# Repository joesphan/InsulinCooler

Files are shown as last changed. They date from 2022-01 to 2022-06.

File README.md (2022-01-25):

# Insulin Cooler

This repository is for my senior project

#### Problem Statement

There is a large population of diabetic citizens who require doses of insulin every day. Long-term portable methods of insulin storage are very expensive.

#### Methodology and Limitations

Insulin must be stored at temperatures from 36&deg;F to 46&deg;F. Using 3d printing to maximalize thermal insulation in the chassis, combined with peltier coolers, lithium-ion batteries and IOT ESP32, it should be reasonably feasible to create a cooler for under $50.

The specs I submitted for my coursework states that the cooler must have a battery life of at least 48 hours. However, I have made it a personal goal to maximize thermal efficiency to achieve two weeks or more.

Using 3d printing, I should be able to create an airgap insulation.

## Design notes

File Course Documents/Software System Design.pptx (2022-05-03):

## Software System Design

EE493
Joesphan Lu

## Summary

Microcontroller Responsibilities
- Insulin temperature regulation
  - Measuring temperature
  - Controlling peltiers
- Datalogging insulin temperature
- Battery management system
  - Battery balancing
- BLE communication
  - Transmission of data and battery status

## Summary (cont’d)

App Responsibilities
- UX – present the user with data
  - Battery status
  - Insulin temperature
    - Realtime and historic

## Tools

- VsCode
  - ESP-IDF SDK for coding, debugging, and flashing
- Gitlab
  - Github desktop for version control frontend
- USB to UART converter
  - FT232RL, CH340G or similar

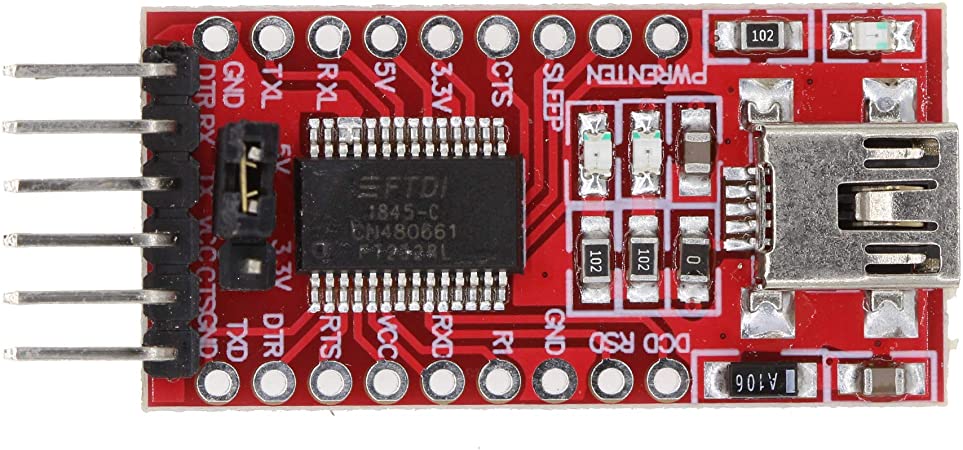
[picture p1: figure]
Amazon.com: FT232RL FTDI USB to TTL 3.3V 5.5V Serial Adapter Module Download Cable for Android Mini Port : Electronics

## MCU Resources

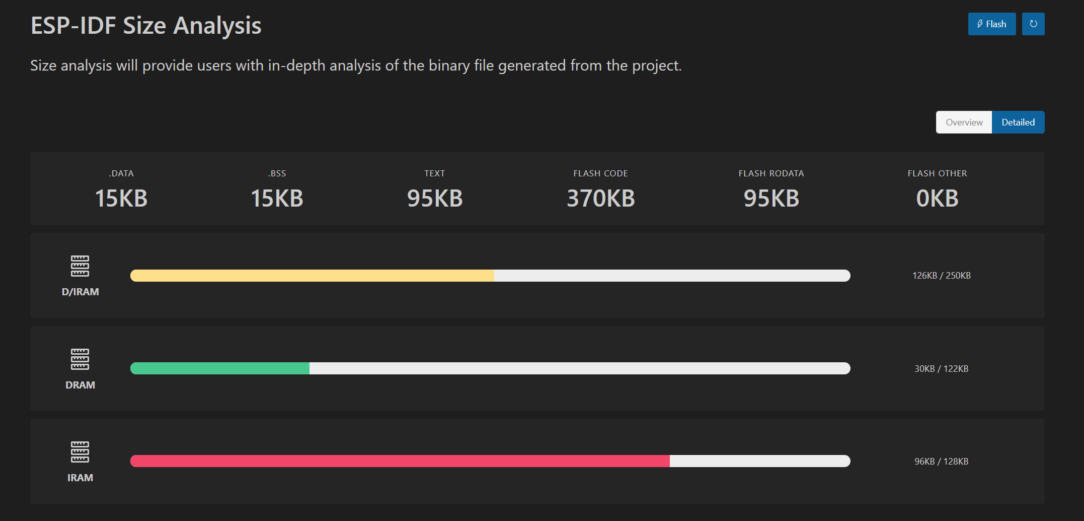
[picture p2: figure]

## Kernel and Task/ISR Design

- freeRTOS
  - BLE SDKs provided by EspressIf use it
  - BLE is the biggest software hurdle
- ISRs:
  - Insulin temperature regulation timer
    - Control peltier coolers on an interval
  - BLE device connection detection
    - Start BLE data transmission
  - USB availability detection
    - Run battery balancing

## Flow-Diagram

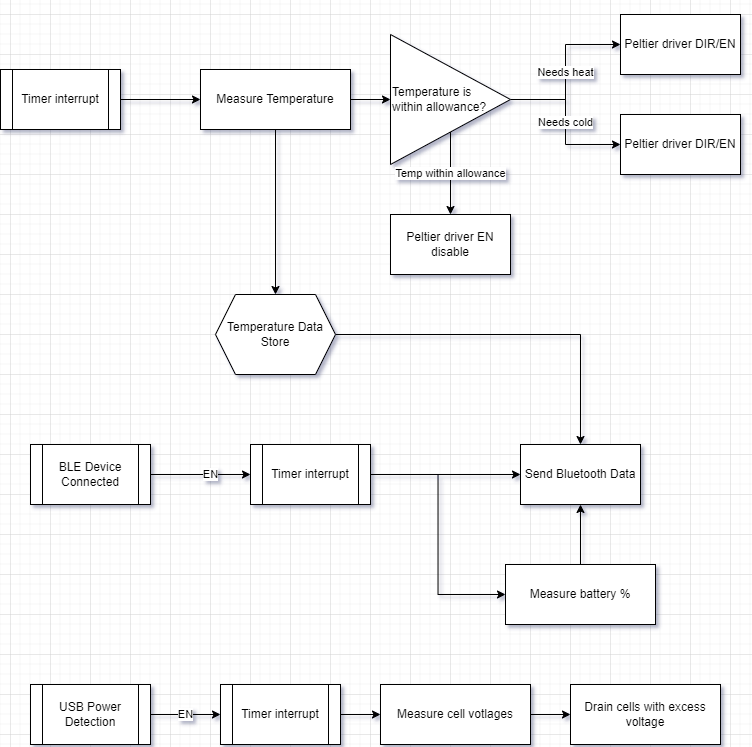
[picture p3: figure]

## Module/Library Description

- TemperatureController
  - Managing temperature of insulin, peltier control
- BatteryMonitor
  - Battery balancing
  - Reads battery percentage
- Datalog
  - Records temperature of insulin to be sent via BLE
- BLESend
  - Send datalogged data to user’s phone

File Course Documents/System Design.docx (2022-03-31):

System Design

Joesphan Lu

BLOCK DIAGRAM

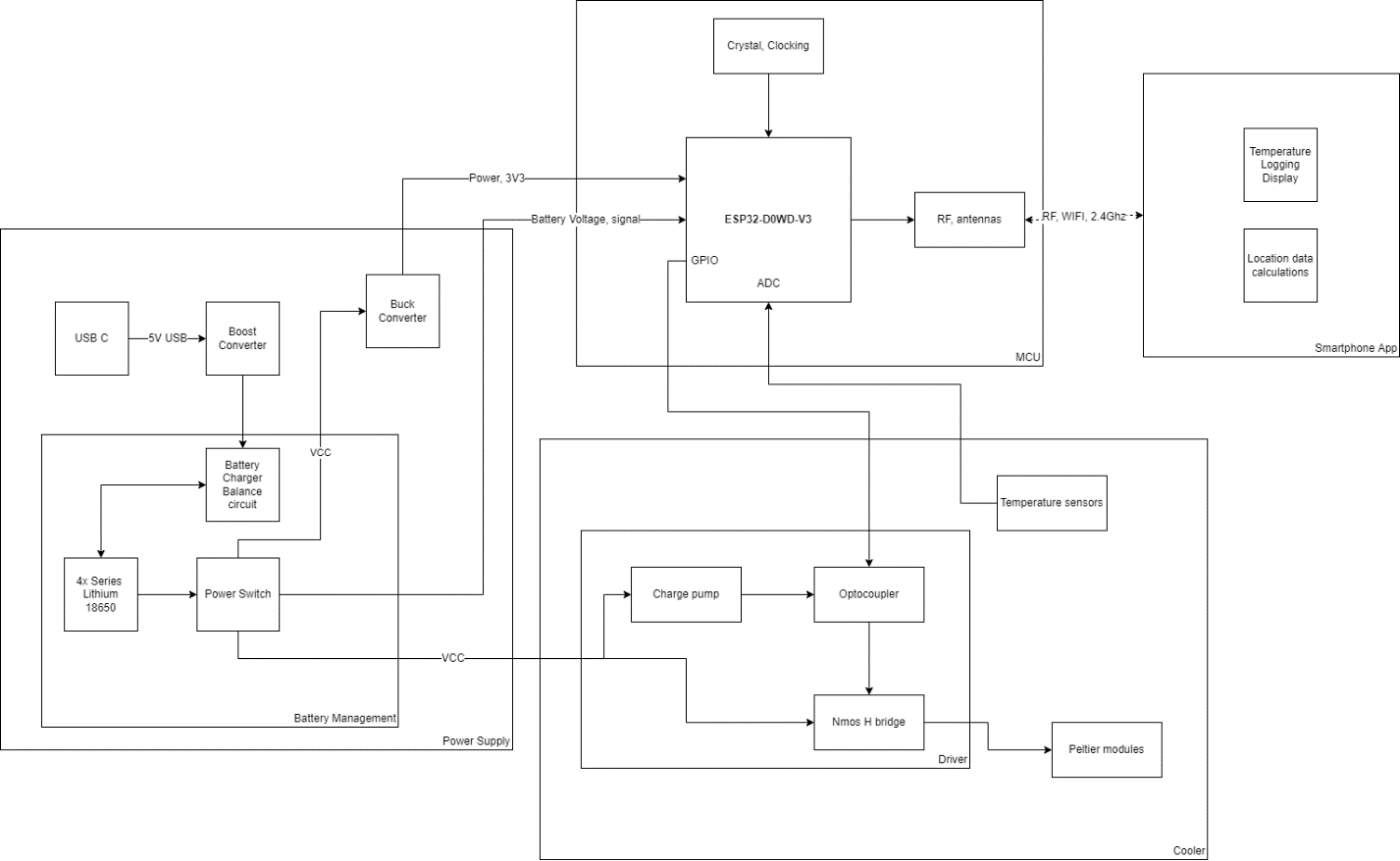
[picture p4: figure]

SUPPLY CURRENTS

Part | Id(3V3) | Id(Unregulated) | Id (USB)
MCU (ESP32-D0WD-V3) ACTIVE RF | 160~260mA | - | -
MCU (ESP32-D0WD-V3) INACTIVE RF | 3~20mA | - | -
Peltier Modules TEC12706 | - | 6A | -
Battery charger | - | - | 3A
Buck converter | - | 0~75mA | -

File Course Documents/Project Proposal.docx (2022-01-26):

Affordable Portable Insulin Cooler

Joesphan Lu

ABSTRACT

The goal of this project is to make an accessible, portable insulin cooler accessible to everybody.

PROBLEM DEFINITION

Insulin coolers on the market today are non-portable and/or very cost prohibitive. Most of them are passive, and not much more than a glorified thermos.

USERS

The users are diabetic people, or anyone who requires insulin to be accessible outside the home, of all financial statuses.

OUTCOMES

Ideally, this project will result in a design that will allow insulin coolers to be accessible to everyone.

FEATURES

-Locating feature, allows user to find the cooler if it’s lost

-Cooling for long periods of time, outperforming passive coolers

-Low cost, affordable to everyone

-Keeps insulin at an appropriate temperature for storage

-Data logging and display available to the user

RISKS

Finding a good compromise between batteries, device longevity, and portability is a major risk, or design challenge. This can be accomplished with more thorough research.

Another risk is the cooling method. Current solutions may not allow efficient cooling. This can be accomplished with running systems at lower duty cycles and/or building a better thermal insulation layer, to achieve higher efficiency.

RESPONSIBILITIES

The device must keep the insulin at an appropriate temperature and must notify the user if the temperature ranges are exceeded. This is critical for the health of the user.

One of the goals of the device is to be low cost. This plays into ethics and making it accessible to everyone.

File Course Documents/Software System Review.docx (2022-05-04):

Software System Review

Joesphan Lu

Summary

The software of the insulin cooler is responsible for controlling the pettier coolers, battery balancing, datalogging, and BLE communications to a phone app.

The phone app is responsible for presenting the user with battery percentage and temperature data.

Tools

Visual Studio code with the ESP-IDF SDK will be used for coding, debugging, and flash programming. Gitlab and Github desktop will be used for revision control.

A generic usb to UART converter will be used as the programmer. CH340G, FT232RL or similar

MCU Resources


On-chip peripherals:

Bluetooth/BLE, PWM, ADC, Radio, RTC/Low Power Management Subsystem

Kernel and Task/ISR design

freeRTOS will be used, as the BLE SDKs by EspressIf use it. The BLE is the biggest software design challenge in this project.

ISRs:

BLE device connection detection, USB power availability, temperature control timer interrupt

Time-Slices TBD

Inter-Task Communications

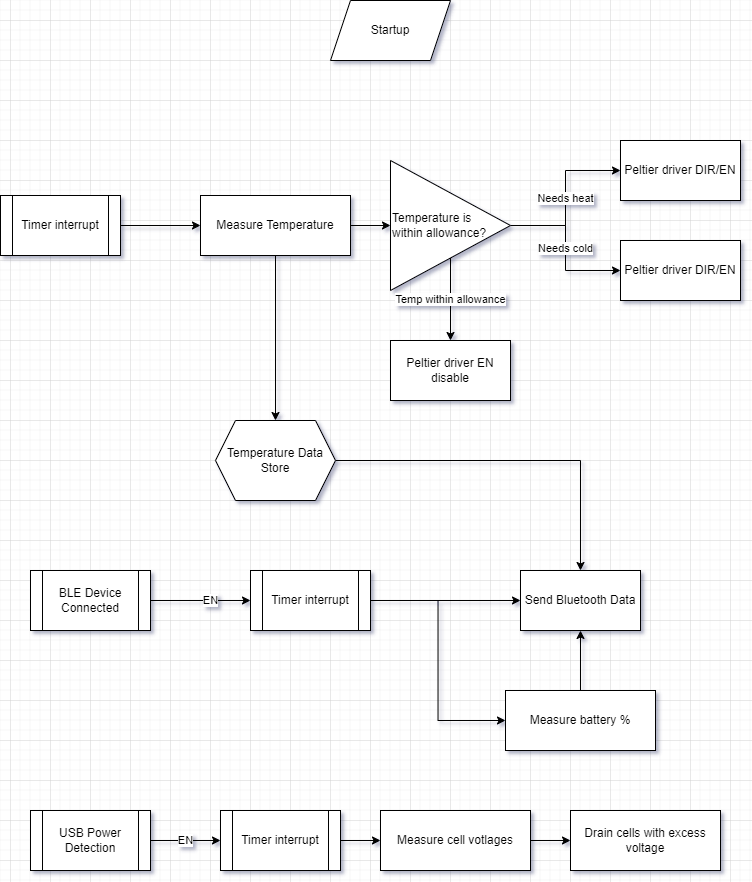
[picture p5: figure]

Module/Library Description

TemperatureControlModule:

Controls temperature of insulin, measures and controls Peltier

BatteryBalancer:

Reads the cell voltage and drains off cells that have excess voltage

BatteryMonitor:

Reads the battery percentage

Datalog:

Records the temperature of insulin, later to be sent via BLE to the mobile device

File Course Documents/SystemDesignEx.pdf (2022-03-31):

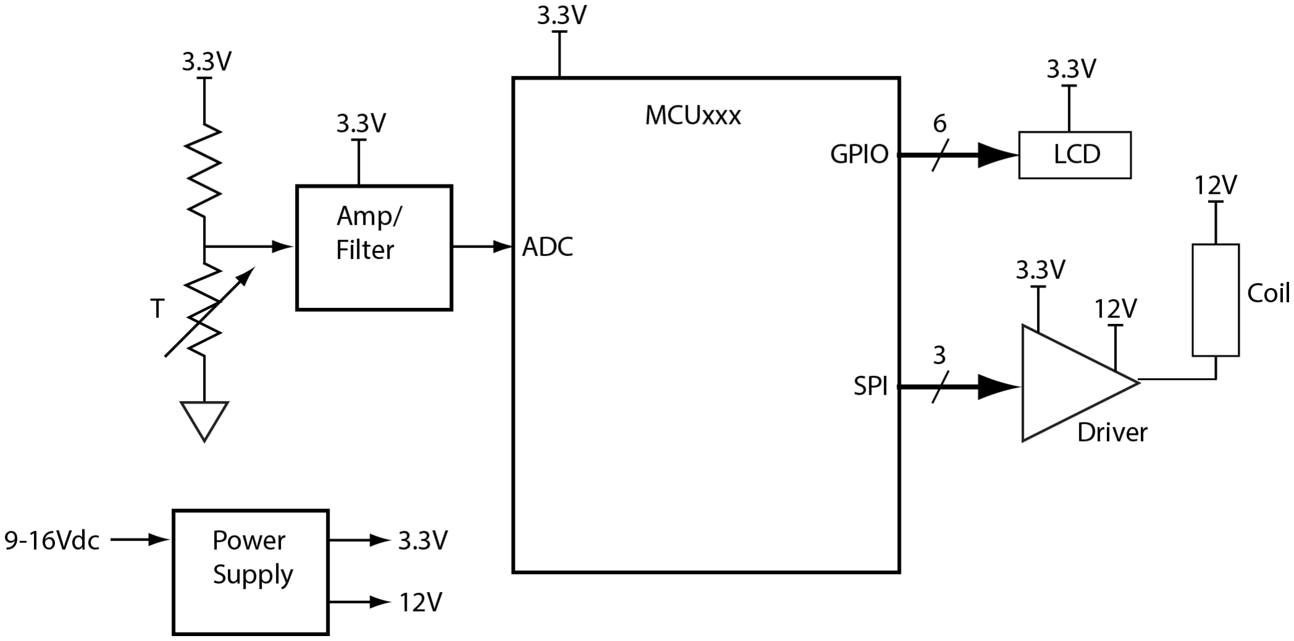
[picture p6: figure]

SystemDesignEx.docx | 1 | 11/23/21

System Design Example

- Based on requirements, the following block diagram was created

Supply Currents

Part | ID (3.3V) | ID (12V) | Dissipation
MCU (K32L2) | 8.7 mA
MCU (K22) | 35.6 mA
LCD | 2.5 mA
OpAmp (LME49721) | 3.25 mA
SallenKey R’s | 4x(3.3/20k)= 660µA
Temp R’s | (10k + 1k) 300µA
MC33879(RUN) | 700 µA | 24 mA | 1.4
MC33879(Sleep) | 700 µA | 5 µA
Coil (20Ω) | | 600 mA
Regulator (Iq)
Total (K32L2) | 16.1 mA | 624 mA

With the numbers shown above, the 3.3V regulator must be able to provide 16.1mA and the 12V regulator (if needed) must provide 624mA.

We still need to determine device power dissipation to see if they’ll get too hot and fail.

SystemDesignEx.docx | 2 | 11/23/21

Power Dissipation
MCU: While the absolute max IO current of +/-25mA, calculations will need to be made to determine if the device will get too hot due to internal R’s in the IOs.

Coil Driver: MC33879, PD, max =1.7W, RDS,on=1.4Ω, Iout,max=1.2A, IxR=1.68W

Coil out, 20ohms, 12/20=600mA, PDIO=600mAx1.4ohms=840mW

150 – 840mWx71 = 90C

Two coils: 30C

Power Supply
- The requirements say that the system must work with a DC input voltage between 9V and 16V

This allows the use of a wide variety of wall adaptors.

- There are two DC output levels required, 3.3V and 12V.
- First, check carefully to see if the coil and driver output supply will work with anything between 9V and 16V. If that is the case, we could go directly to the source without voltage regulation.

Many coil-type devices, solenoids, relays, motors, etc, may work over a wide range of voltages. It may even be worth a reduction in input voltage range if requirements allow.

Regulator 1 – 3.3V, 20mA out, Linear
- Linear – low cost, small size.
- Power out: 3.3 x 20mA = 66mW
- Power in: 16 x 20mA = 320mW
- Power dissipation in regulator: 254mW + Iq
- Efficiency: 66mW/254mW = 26% !

Regulator 1 – 3.3V, 20mA out, Switching
- Power out: 3.3 x 20mA = 66mW
- Efficiency: 85%
- Power in: 77mW, 16 V -> 4.9mA
- Power dissipation in regulator: 11mW + Iq

SystemDesignEx.docx | 3 | 11/23/21

Battery Life
- Requirement: 4 weeks
- Assume coil duty cycle is 0.1, Iavg = 60mA
- Regulator 2, buck-boost, 80% efficient, 75mA in.
- What size battery in mAHr?

With linear regulator 1: Iin = 75mA+20mA = 95mA

Requires: 95mA x 672Hr = 65mAHr

With switching regulator 1: Iin = 75mA+4.9mA = 80mA

Requires: 80mA x 672Hr = 54mAHr

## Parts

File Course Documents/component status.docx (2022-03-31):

Joesphan Lu

Senior Project Component Status

1/20/2022

MFG/SKU | Datasheet packing dwg | Footprint | Symbol

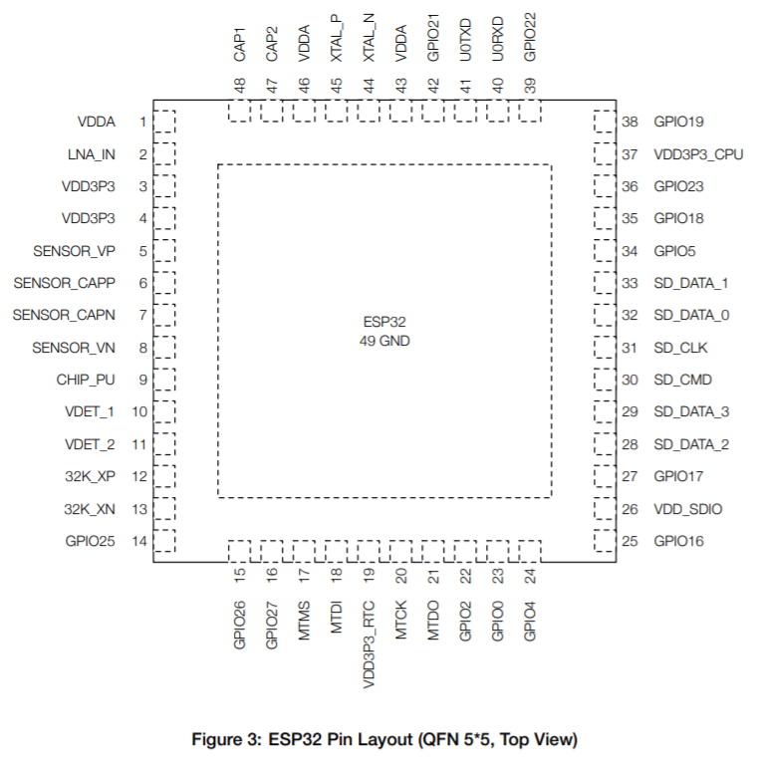
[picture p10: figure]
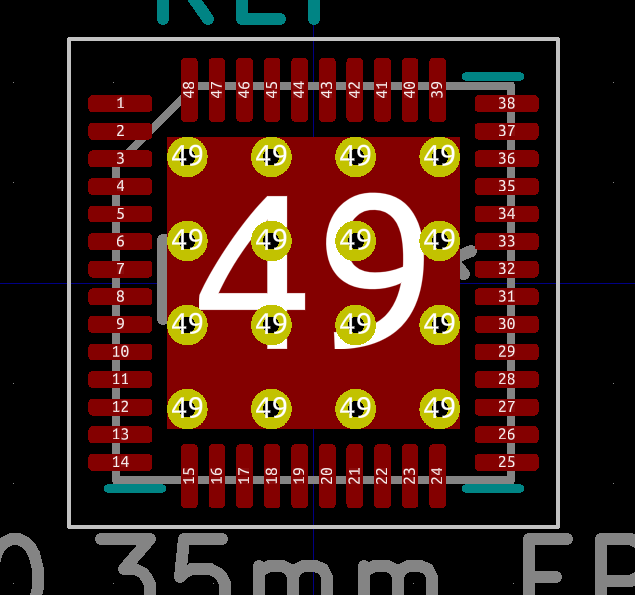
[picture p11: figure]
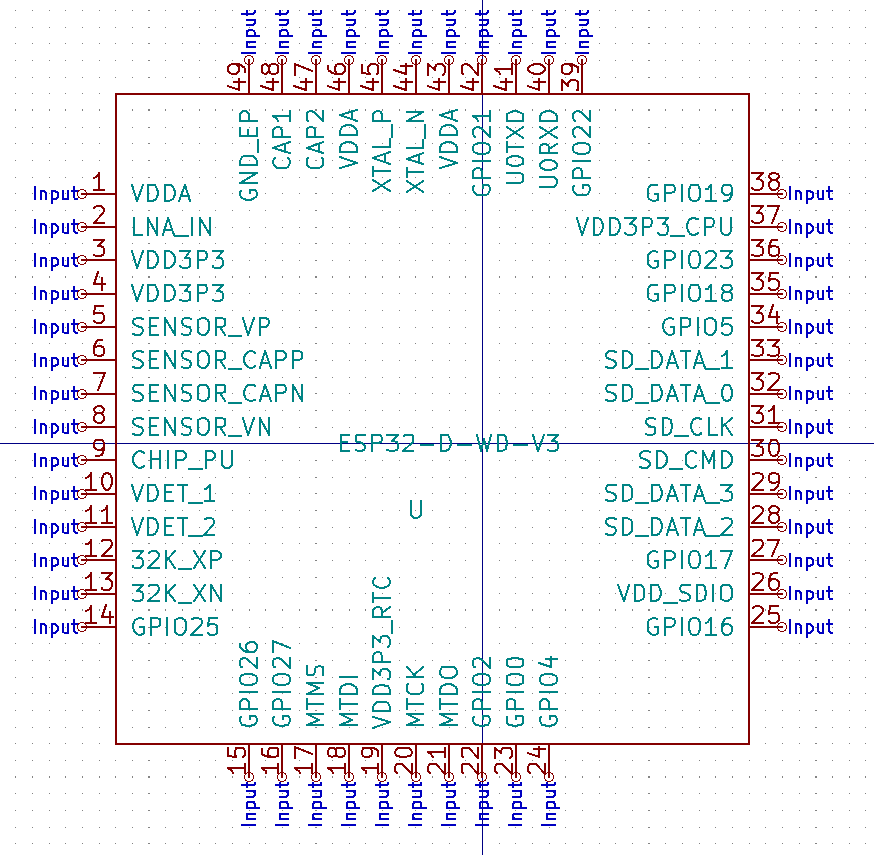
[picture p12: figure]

Espressif ESP32-D0WD-V3

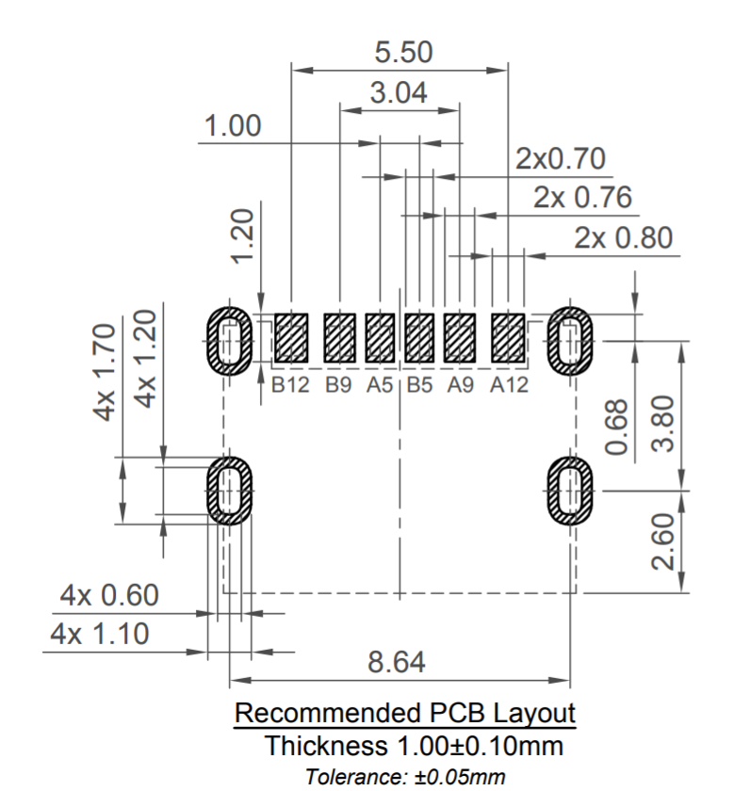
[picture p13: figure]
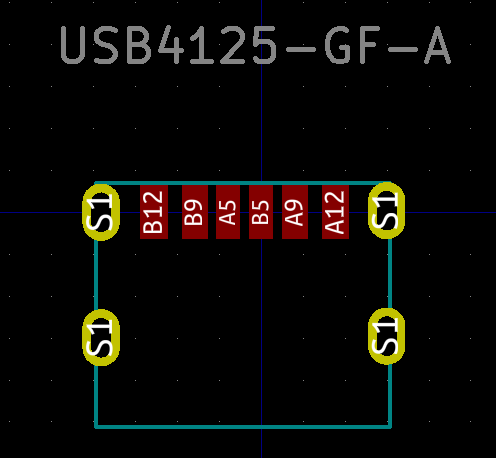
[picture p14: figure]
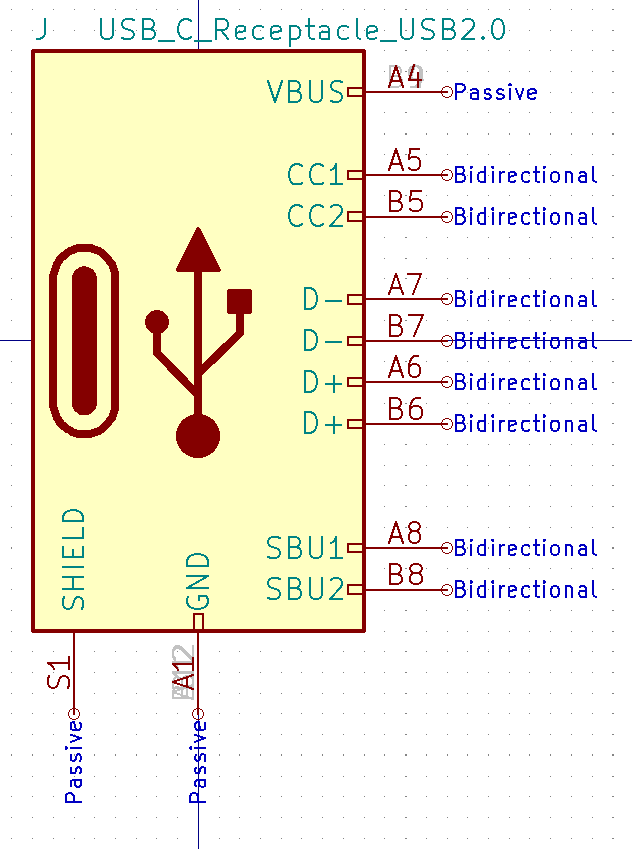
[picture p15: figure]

GCT USB4125-GF-A

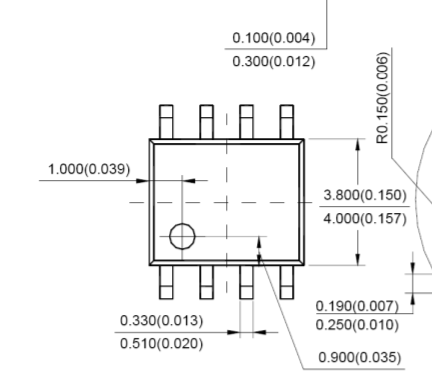
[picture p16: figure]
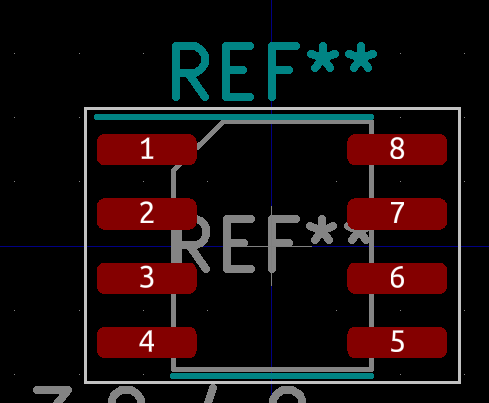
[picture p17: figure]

MaxLinear, Inc. SP34063AEN-L/TR


Raltron Electronics RH100-40.000-10-F-1010-TR


Nexperia USA Inc. BUK9K52-60E | | | Unit A: Unit B:


International Rectifier IRS2103SPBF
Battery charger TBD
Peltier cooler | 2 wires | 1x2 header | 1x2 header

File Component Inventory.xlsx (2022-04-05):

Manufacturer Part Number | Description | Unit Price | Extended Price | Quantity | Ouchies
MIKROE-3828 | PELTIER ELEMENT TEC1-12706 | 5 | $10.00 | 2 | $87.83
ESP32-D0WD-V3 | IC RF TXRX+MCU BLUETOOTH WIFI | 1.8 | $5.40 | 3
USB4125-GF-A | CONN RCPT TYPE C 6P SMD RA | 0.7 | $3.50 | 5
2108838-1 | CHIP ANT., SMD, BT/WI-FI 2.4GHZ | 0.42 | $1.26 | 3
SP34063AEN-L/TR | IC REG BUCK BST ADJ 1.5A 8SOIC | 0.55 | $1.65 | 3
CL32A107MQVNNNE | CAP CER 100UF 6.3V X5R 1210 | 0.68 | $2.04 | 3
SDES064T-221MS | FIXED IND 220UH 640MA 1.04OHM SM | 0.41 | $2.05 | 5
RH100-40.000-10-F-1010-TR | CRYSTAL 40.0000MHZ 10PF SMD | 0.39 | $1.56 | 4
SDNT2012X103F3950FTF | THERM NTC 10KOMH 3950K 0805 | 0.1296 | $3.24 | 25
1N5819-TP | DIODE SCHOTTKY 40V 1A DO41 | 0.264 | $2.64 | 10
73L2R20J | RES 0.2 OHM 5% 1/10W 0603 | 0.086 | $0.86 | 10
BUK9K52-60E,115 | MOSFET 2N-CH 60V 16A LFPAK56D | 0.95 | $3.80 | 4
PAM2305DGFADJ | IC REG BUCK ADJUSTABLE 1A 6DFN | 0.398 | $3.98 | 10
104CDMCCDS-330MC | FIXED IND 33UH 4.1A 92 MOHM SMD | 1.08 | $5.40 | 5
AS431BNTR-G1 | IC VREF SHUNT ADJ 1% SOT23-3 | 0.257 | $2.57 | 10
BSD316SNL6327XT | MOSFET N-CH 30V 1.4A SOT363-6 | 0.105 | $10.50 | 100
MCR100JZHF28R7 | RES SMD 28.7 OHM 1% 1W 2512 | 0.242 | $2.42 | 10
KDV12FR100ET | RES 0.1 OHM 1% 1/2W 1206 | 0.264 | $2.64 | 10
SLG55021-200010V | IC GATE DRVR HIGH-SIDE 8TDFN | 0.4552 | $11.38 | 25
AOZ6662DI | POWER IC EZBUCK | 0.4376 | $10.94 | 25

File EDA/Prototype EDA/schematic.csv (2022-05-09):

Source: | C:\Users\joesp\Documents\GitHub\InsulinCooler\EDA\Prototype EDA\schematic.kicad_sch
Date: | 5/7/2022 4:36:04 AM
Tool: | Eeschema (6.0.2)
Generator: | C:\Program Files\KiCad\6.0\bin\scripting\plugins/bom_csv_grouped_by_value_with_fp.py
Component Count: | 97
Ref | Qnty | Value | Cmp name | Footprint | Description | Vendor
AE1, | 1 | Antenna_Chip | Antenna_Chip | RF_Antenna:Johanson_2450AT18x100 | Ceramic chip antenna with pin for PCB trace
BT1, BT2, BT3, | 3 | Battery_Cell | Battery_Cell | Connector_PinHeader_2.54mm:PinHeader_1x02_P2.54mm_Vertical | Single-cell battery
C1, | 1 | 3.797pF | C | Capacitor_SMD:C_0805_2012Metric_Pad1.18x1.45mm_HandSolder | Unpolarized capacitor
C2, | 1 | 4.64pF | C | Capacitor_SMD:C_0805_2012Metric_Pad1.18x1.45mm_HandSolder | Unpolarized capacitor
C3, | 1 | 3.3nF | C | Capacitor_SMD:C_0805_2012Metric_Pad1.18x1.45mm_HandSolder | Unpolarized capacitor
C4, | 1 | 10nF | C | Capacitor_SMD:C_0805_2012Metric_Pad1.18x1.45mm_HandSolder | Unpolarized capacitor
C5, C8, C10, C11, C16, C17, C21, | 7 | 100nF | C | Capacitor_SMD:C_0805_2012Metric_Pad1.18x1.45mm_HandSolder | Unpolarized capacitor
C6, C7, | 2 | 10pF | C | Capacitor_SMD:C_0805_2012Metric_Pad1.18x1.45mm_HandSolder | Unpolarized capacitor
C9, C12, C15, | 3 | 10uF | C | Capacitor_SMD:C_0805_2012Metric_Pad1.18x1.45mm_HandSolder | Unpolarized capacitor
C13, C14, | 2 | 22uF | C | Capacitor_SMD:C_0805_2012Metric_Pad1.18x1.45mm_HandSolder | Unpolarized capacitor
C18, | 1 | 1uF | C | Capacitor_SMD:C_0805_2012Metric_Pad1.18x1.45mm_HandSolder | Unpolarized capacitor
D4, | 1 | SS34 | D_Schottky | Diode_SMD:D_SMA_Handsoldering | Schottky diode
J1, | 1 | Peltier Connection | Conn_01x02_Female | Connector_PinHeader_2.54mm:PinHeader_1x02_P2.54mm_Vertical | Generic connector, single row, 01x02, script generated (kicad-library-utils/schlib/autogen/connector/)
J2, | 1 | USB_C_Receptacle_USB2.0 | USB_C_PWR_ONLY | 1KicadLib:USB4125-GF-A
J3, J5, J6, J7, J8, | 5 | Conn_01x01_Male | Conn_01x01_Male | 1KicadLib:GatorTestpoint | Generic connector, single row, 01x01, script generated (kicad-library-utils/schlib/autogen/connector/)
J4, J9, J10, J11, | 4 | PROG_PORT | Conn_01x02_Male | Connector_PinHeader_2.54mm:PinHeader_1x02_P2.54mm_Vertical | Generic connector, single row, 01x02, script generated (kicad-library-utils/schlib/autogen/connector/)
L1, | 1 | 1.807nH | L | Inductor_SMD:L_0805_2012Metric_Pad1.15x1.40mm_HandSolder | Inductor
L2, | 1 | 3.3uH NRS5024T3R3NMGJ | L | Inductor_SMD:L_Taiyo-Yuden_NR-50xx_HandSoldering | Inductor
L3, | 1 | 33uH | L | Inductor_SMD:L_10.4x10.4_H4.8 | Inductor
R1, R10, | 2 | 20k | R | Resistor_SMD:R_0805_2012Metric_Pad1.20x1.40mm_HandSolder | Resistor
R2, R3, | 2 | 0 | R | Resistor_SMD:R_0805_2012Metric_Pad1.20x1.40mm_HandSolder | Resistor
R4, | 1 | .1 | R | Resistor_SMD:R_1206_3216Metric_Pad1.30x1.75mm_HandSolder | Resistor
R5, R6, | 2 | 1k | R | Resistor_SMD:R_0805_2012Metric_Pad1.20x1.40mm_HandSolder | Resistor
R7, R34, | 2 | 12.5k | R | Resistor_SMD:R_0805_2012Metric_Pad1.20x1.40mm_HandSolder | Resistor
R8, R9, | 2 | 5.1k | R | Resistor_SMD:R_0805_2012Metric_Pad1.20x1.40mm_HandSolder | Resistor
R12, R15, R16, | 3 | 28.7 | R | Resistor_SMD:R_2512_6332Metric_Pad1.40x3.35mm_HandSolder | Resistor
R17, R18, R19, | 3 | 200 | R | Resistor_SMD:R_0805_2012Metric_Pad1.20x1.40mm_HandSolder | Resistor
R20, R21, R24, | 3 | 90k | R | Resistor_SMD:R_0805_2012Metric_Pad1.20x1.40mm_HandSolder | Resistor
R22, R26, | 2 | 180k | R | Resistor_SMD:R_0805_2012Metric_Pad1.20x1.40mm_HandSolder | Resistor
R23, | 1 | 36k | R | Resistor_SMD:R_0805_2012Metric_Pad1.20x1.40mm_HandSolder | Resistor
R25, | 1 | 4.3k | R | Resistor_SMD:R_0805_2012Metric_Pad1.20x1.40mm_HandSolder | Resistor
R27, | 1 | 68k | R | Resistor_SMD:R_0805_2012Metric_Pad1.20x1.40mm_HandSolder | Resistor
R28, | 1 | 510k | R | Resistor_SMD:R_0805_2012Metric_Pad1.20x1.40mm_HandSolder | Resistor
R29, | 1 | 620k | R | Resistor_SMD:R_0805_2012Metric_Pad1.20x1.40mm_HandSolder | Resistor
R30, | 1 | 200k | R | Resistor_SMD:R_0805_2012Metric_Pad1.20x1.40mm_HandSolder | Resistor
R31, | 1 | 51k | R | Resistor_SMD:R_0805_2012Metric_Pad1.20x1.40mm_HandSolder | Resistor
R33, | 1 | 500 | R | Resistor_SMD:R_0805_2012Metric_Pad1.20x1.40mm_HandSolder | Resistor
R39, | 1 | 150k | R | Resistor_SMD:R_0805_2012Metric_Pad1.20x1.40mm_HandSolder | Resistor
R40, | 1 | 100k | R | Resistor_SMD:R_0805_2012Metric_Pad1.20x1.40mm_HandSolder | Resistor
SW1, | 1 | Power Switch | SW_DIP_x01 | Connector_PinHeader_2.54mm:PinHeader_1x02_P2.54mm_Vertical | 1x DIP Switch, Single Pole Single Throw (SPST) switch, small symbol
TH1, TH2, TH3, | 3 | SDNT2012X103F3950FTF | Thermistor | Resistor_SMD:R_0805_2012Metric_Pad1.20x1.40mm_HandSolder | Temperature dependent resistor
U1, | 1 | ESP32-D-WD-V3 | ESP32-D-WD-V3 | Package_DFN_QFN:QFN-48-1EP_5x5mm_P0.35mm_EP3.7x3.7mm
U2, U7, U8, | 3 | NL17SZ14 | NL17SZ14 | Package_TO_SOT_SMD:SOT-553
U3, U4, | 2 | DMT3020LSDQ | DMT3020LSDQ | Package_SO:SO-8_3.9x4.9mm_P1.27mm
U5, | 1 | LM324 | LM324 | Package_SO:SOIC-14_3.9x8.7mm_P1.27mm | Low-Power, Quad-Operational Amplifiers, DIP-14/SOIC-14/SSOP-14
U6, U18, | 2 | slg55021 | slg55021 | 1KicadLib:TDFN_8_2x2mm_EP_0.9x1.65mm
U9, U10, U11, U20, U21, | 5 | BSD316 | BSD316 | Package_TO_SOT_SMD:SOT-363_SC-70-6_Handsoldering
U12, U13, U14, | 3 | PC817 | PC817 | Package_DIP:DIP-4_W7.62mm | DC Optocoupler, Vce 35V, CTR 50-300%, DIP-4
U15, | 1 | AS431 | AS431 | Package_TO_SOT_SMD:SOT-23-5_HandSoldering
U16, | 1 | AP63203WU | AP63203WU | Package_TO_SOT_SMD:TSOT-23-6 | 2A, 1.1MHz Buck DC/DC Converter, fixed 3.3V output voltage, TSOT-23-6
U17, | 1 | XL6009 | XL6009 | Package_TO_SOT_SMD:TO-263-5_TabPin3
U19, | 1 | HT75xx-1-SOT89 | HT75xx-1-SOT89 | Package_TO_SOT_SMD:SOT-89-3 | 100mA Low Dropout Voltage Regulator, Fixed Output, SOT89
U22, | 1 | W25Q40CL | W25Q40CL | Package_SO:SOIC-8W_5.3x5.3mm_P1.27mm
Y1, | 1 | Crystal_GND24 | Crystal_GND24 | Crystal:Crystal_SMD_SeikoEpson_FA238-4Pin_3.2x2.5mm_HandSoldering | Four pin crystal, GND on pins 2 and 4

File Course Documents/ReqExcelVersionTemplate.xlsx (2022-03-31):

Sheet: Summary
Requirement Number and Version | Approved | Verf Required | Verf Plan | Verf Done | Verf Met | Requirement | Comments
1.a | 0.000 |  |  |  |  | The portable insulin cooler shall be able to charge via USB
1.1.a | 0.000 |  |  |  |  | 0.000
2.a | 0.000 |  |  |  |  | The portable insulin cooler must fit in a pair of Calvin Klein 34x34 jeans
3.a | 0.000 |  |  |  |  | The portable insulin cooler shall hold 5 or more cartridges
4.a | 0.000 |  |  |  |  | The portable insulin cooler shall have a location tracking method
5.a | 0.000 |  |  |  |  | The portable insulin cooler shall have a temperature logging and display
6.a | 0.000 |  |  |  |  | The battery needs to last at least 24 hours

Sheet: 1.a
User Requirement
Project Name: | Portable Insulin Cooler
Originator: | Joesphan Lu
Approved:
User Requirement Text: | The portable insulin cooler shall be able to charge via USB
Rationale: | USB is convienient

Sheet: 1.1.a
Technical Requirement | TEMPLATE
Project Name:
Originator:
Approved:
User Requirement Text:
Rationale and Assumptions:
Verification Required:
Verification Plan and Verification Data:

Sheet: 2.a
User Requirement
Project Name: | Portable Insulin Cooler
Originator: | Joesphan Lu
Approved:
User Requirement Text: | The portable insulin cooler must fit in a pair of Calvin Klein 34x34 jeans
Rationale: | Must be portable enough

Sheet: 3.a
User Requirement
Project Name: | Portable Insulin Cooler
Originator: | Joesphan Lu
Approved:
User Requirement Text: | The portable insulin cooler shall hold 5 or more cartridges
Rationale: | Reasonably sized supply

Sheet: 4.a
User Requirement
Project Name: | Portable Insulin Cooler
Originator: | Joesphan Lu
Approved:
User Requirement Text: | The portable insulin cooler shall have a location tracking method
Rationale: | In case it be lost, one can find relatively quickly

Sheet: 5.a
User Requirement
Project Name: | Portable Insulin Cooler
Originator: | Joesphan Lu
Approved:
User Requirement Text: | The portable insulin cooler shall have a temperature logging and display
Rationale: | The user needs to be able to decide if they the insulin has been appropriately refrigerated

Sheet: 6.a
User Requirement
Project Name: | Portable Insulin Cooler
Originator: | Joesphan Lu
Approved:
User Requirement Text: | The battery needs to last at least 24 hours
Rationale: | Long enough to get through a day

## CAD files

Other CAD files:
Chassis 3d model/OldVersions/main.0001.ipt
Chassis 3d model/main.ipt
Part1.ipt

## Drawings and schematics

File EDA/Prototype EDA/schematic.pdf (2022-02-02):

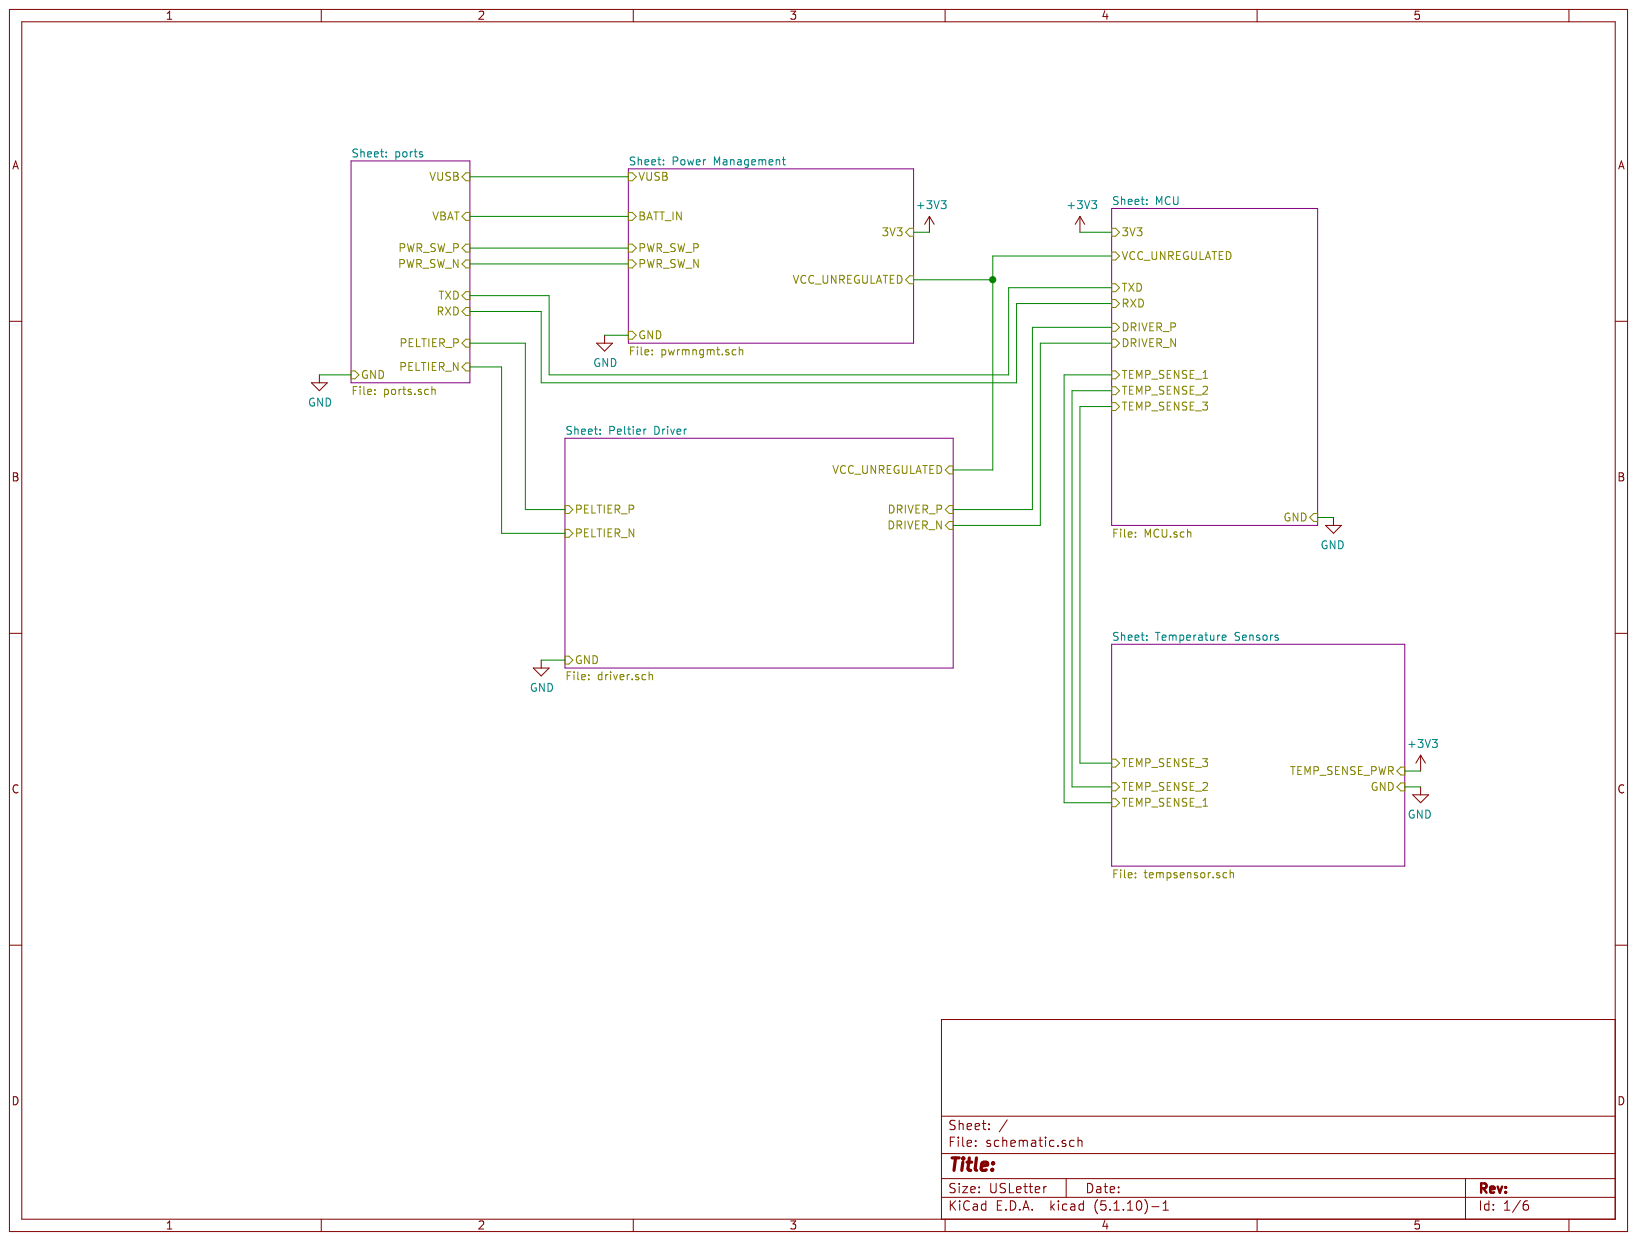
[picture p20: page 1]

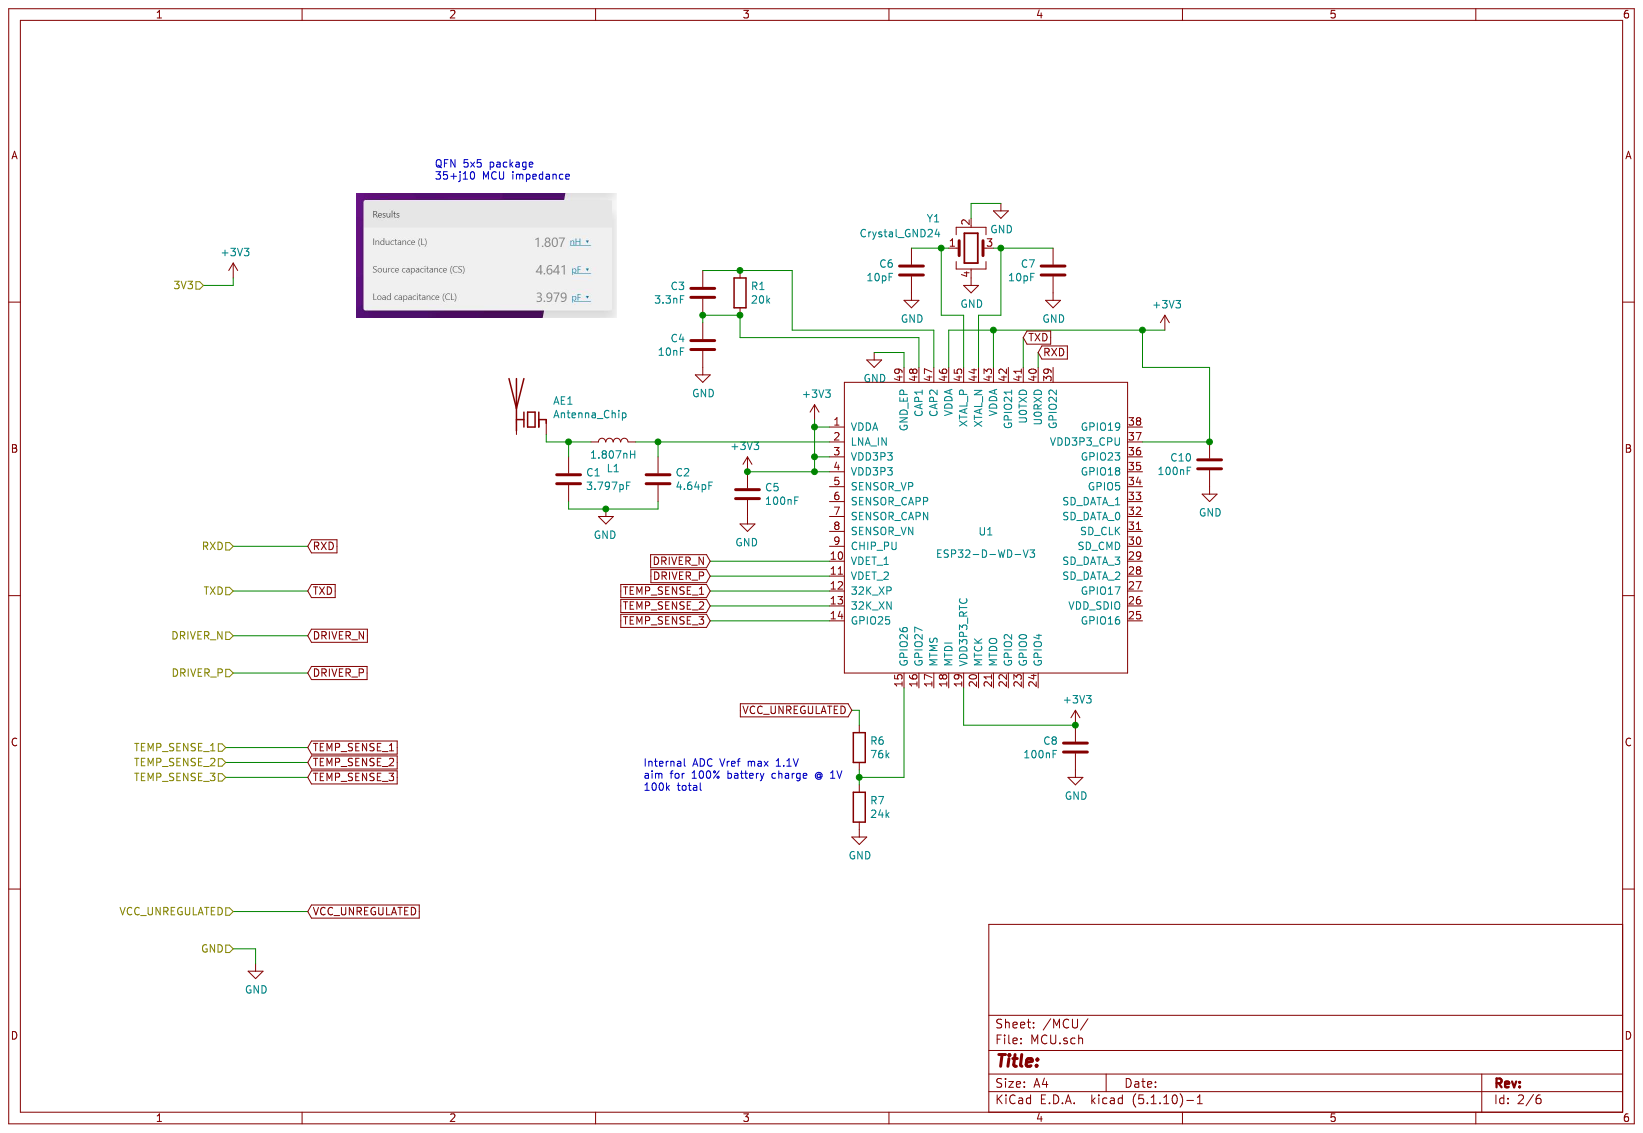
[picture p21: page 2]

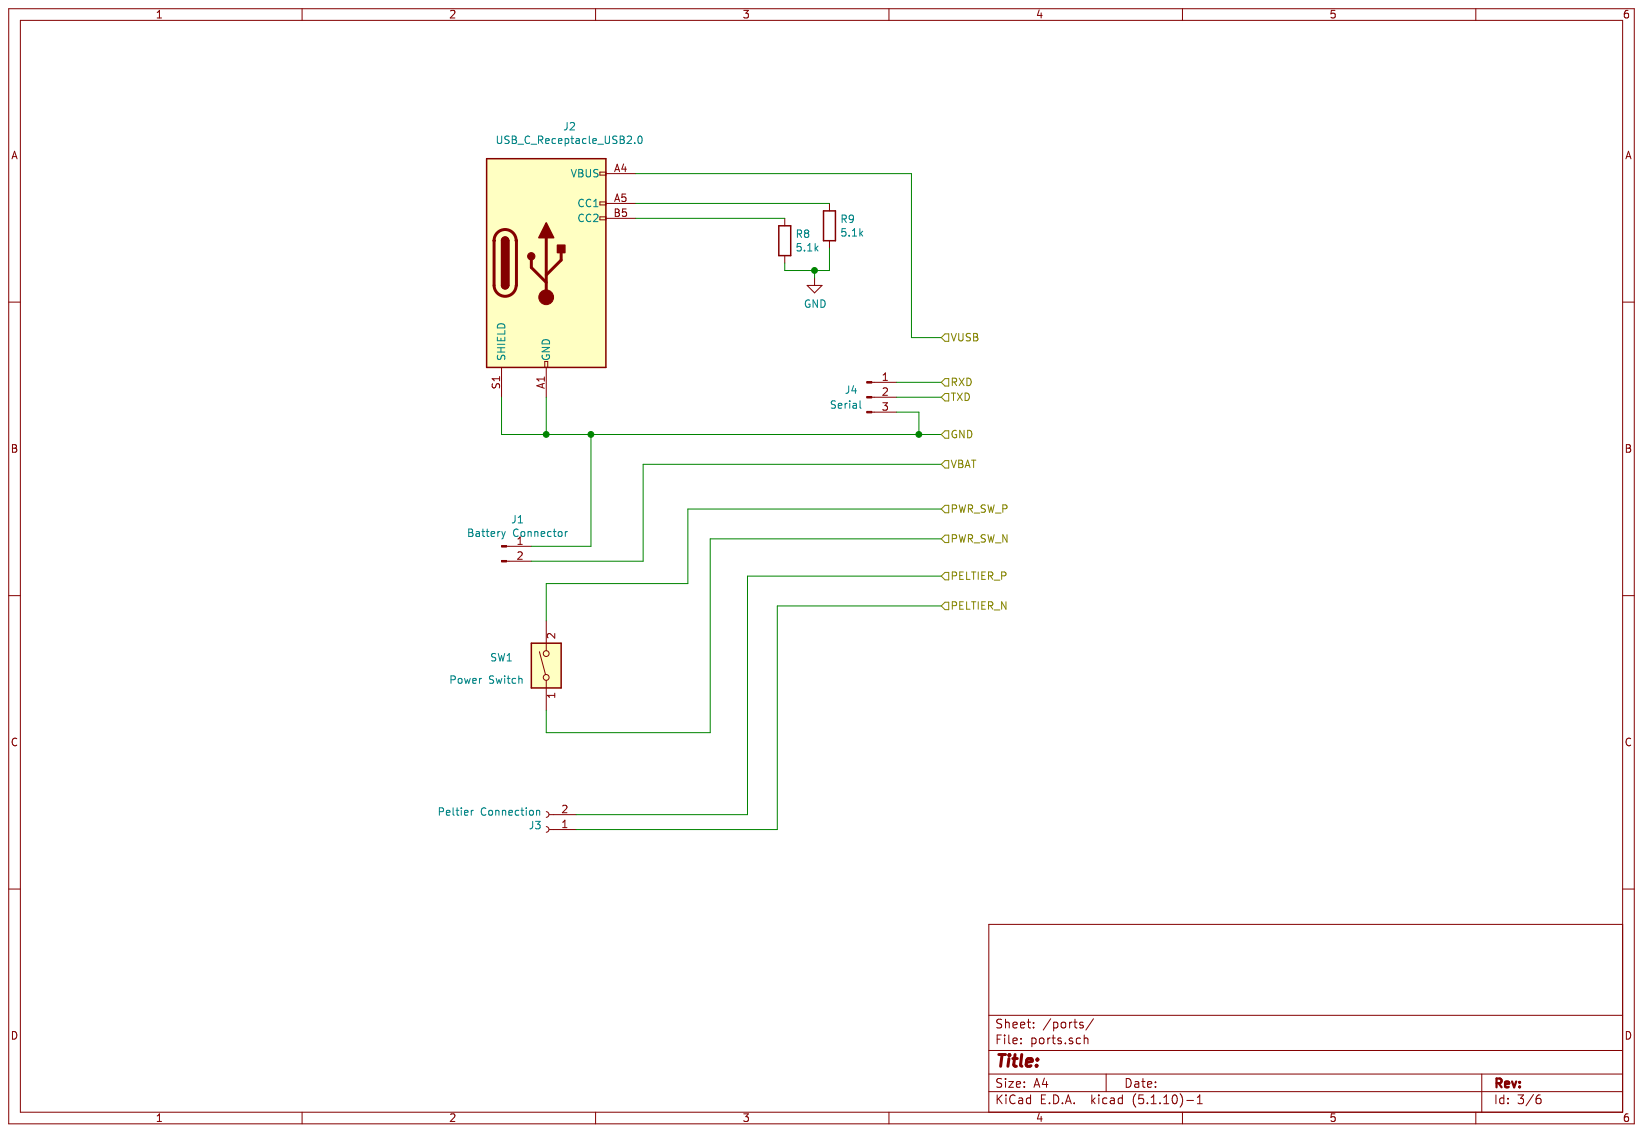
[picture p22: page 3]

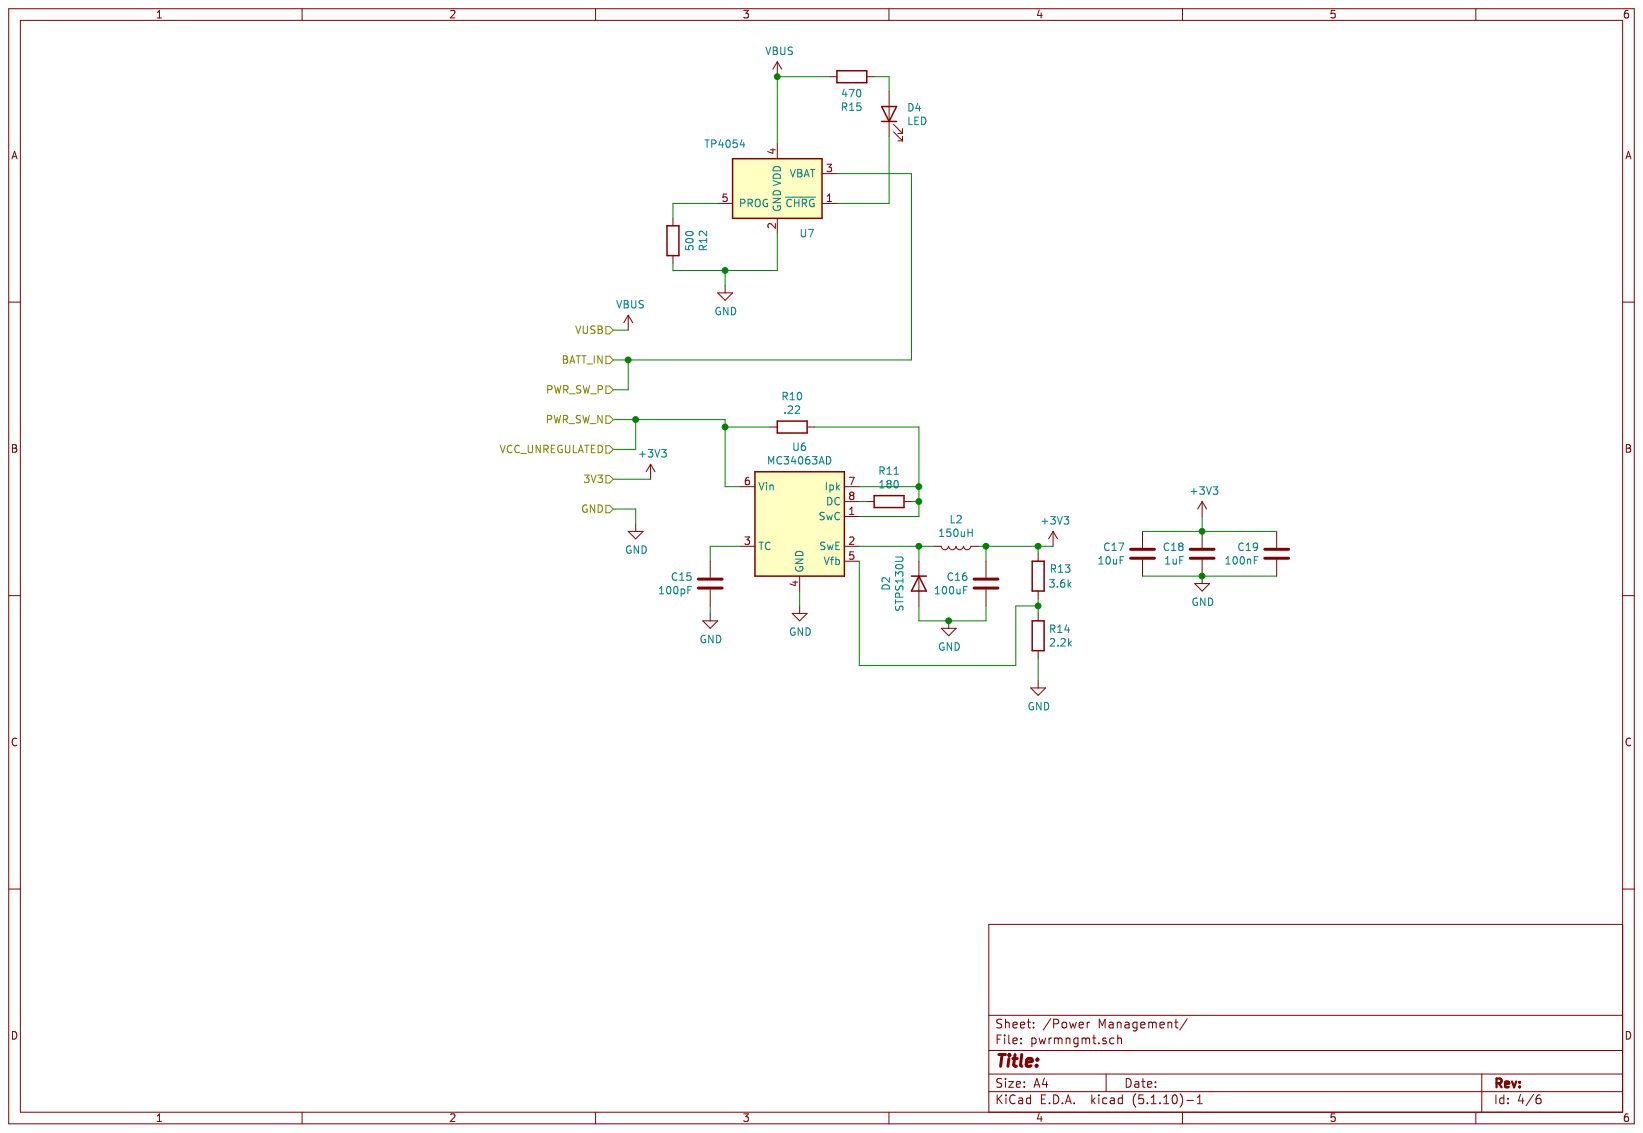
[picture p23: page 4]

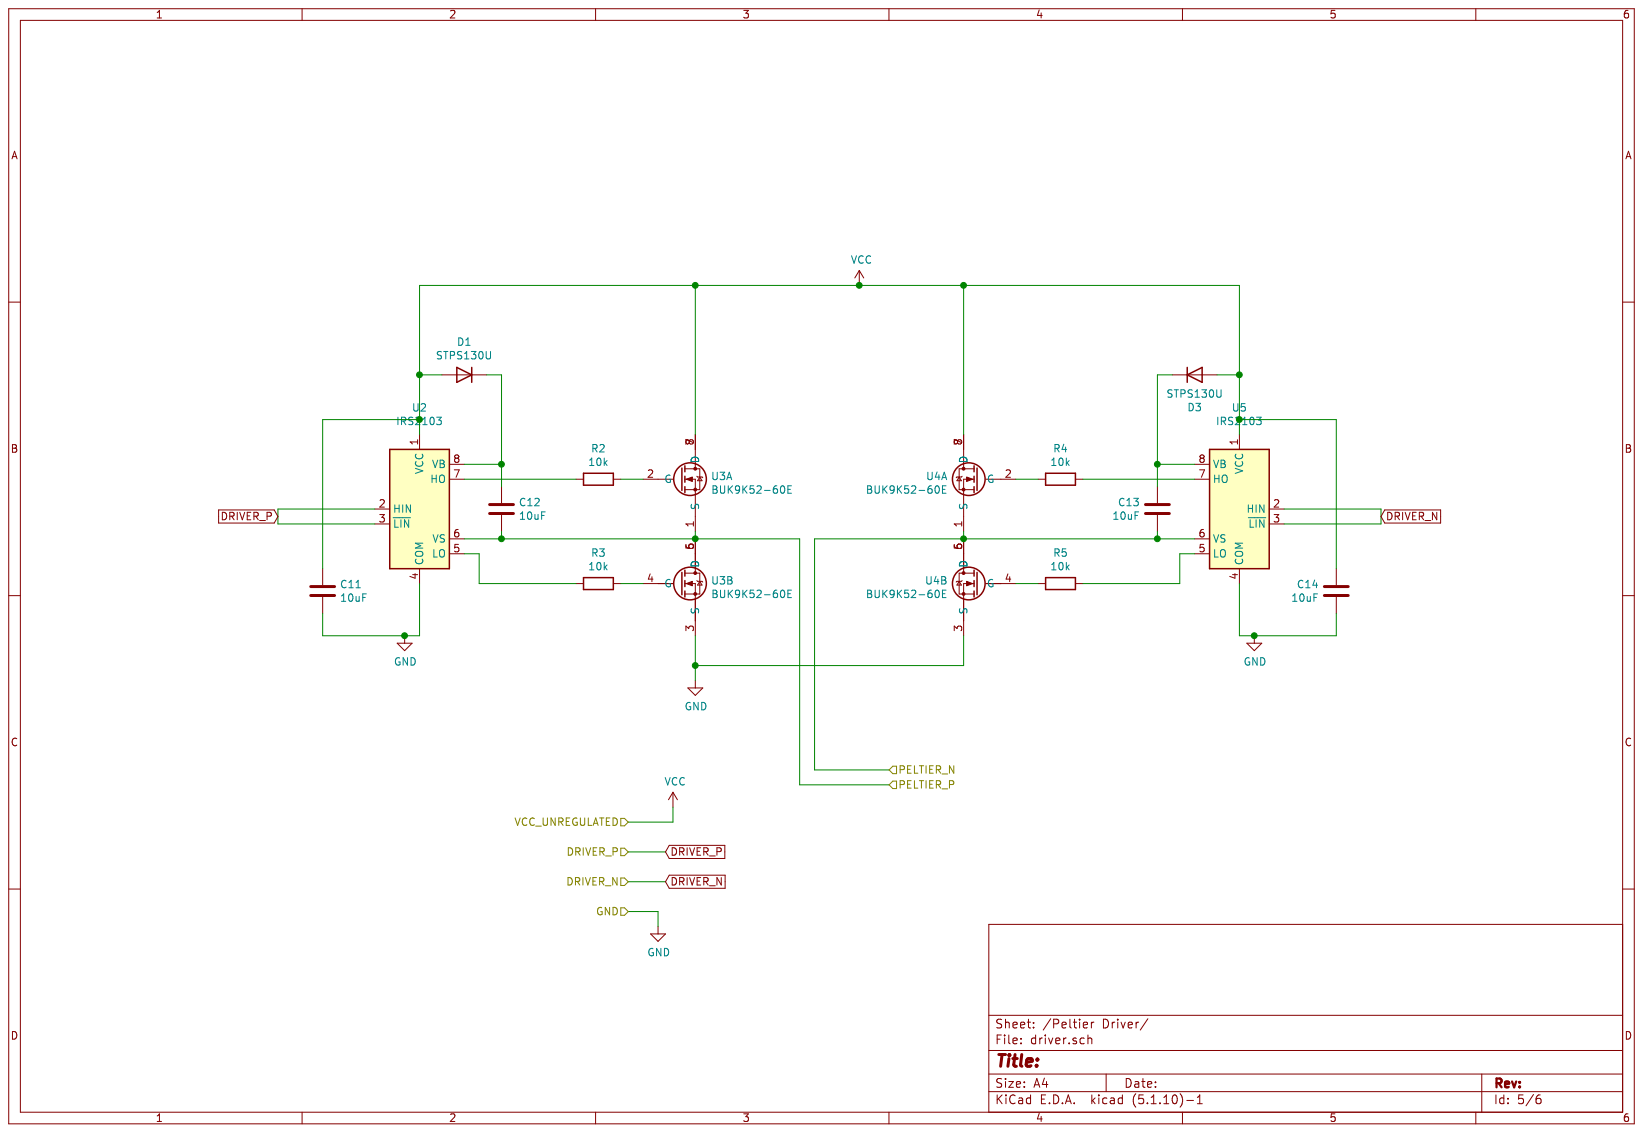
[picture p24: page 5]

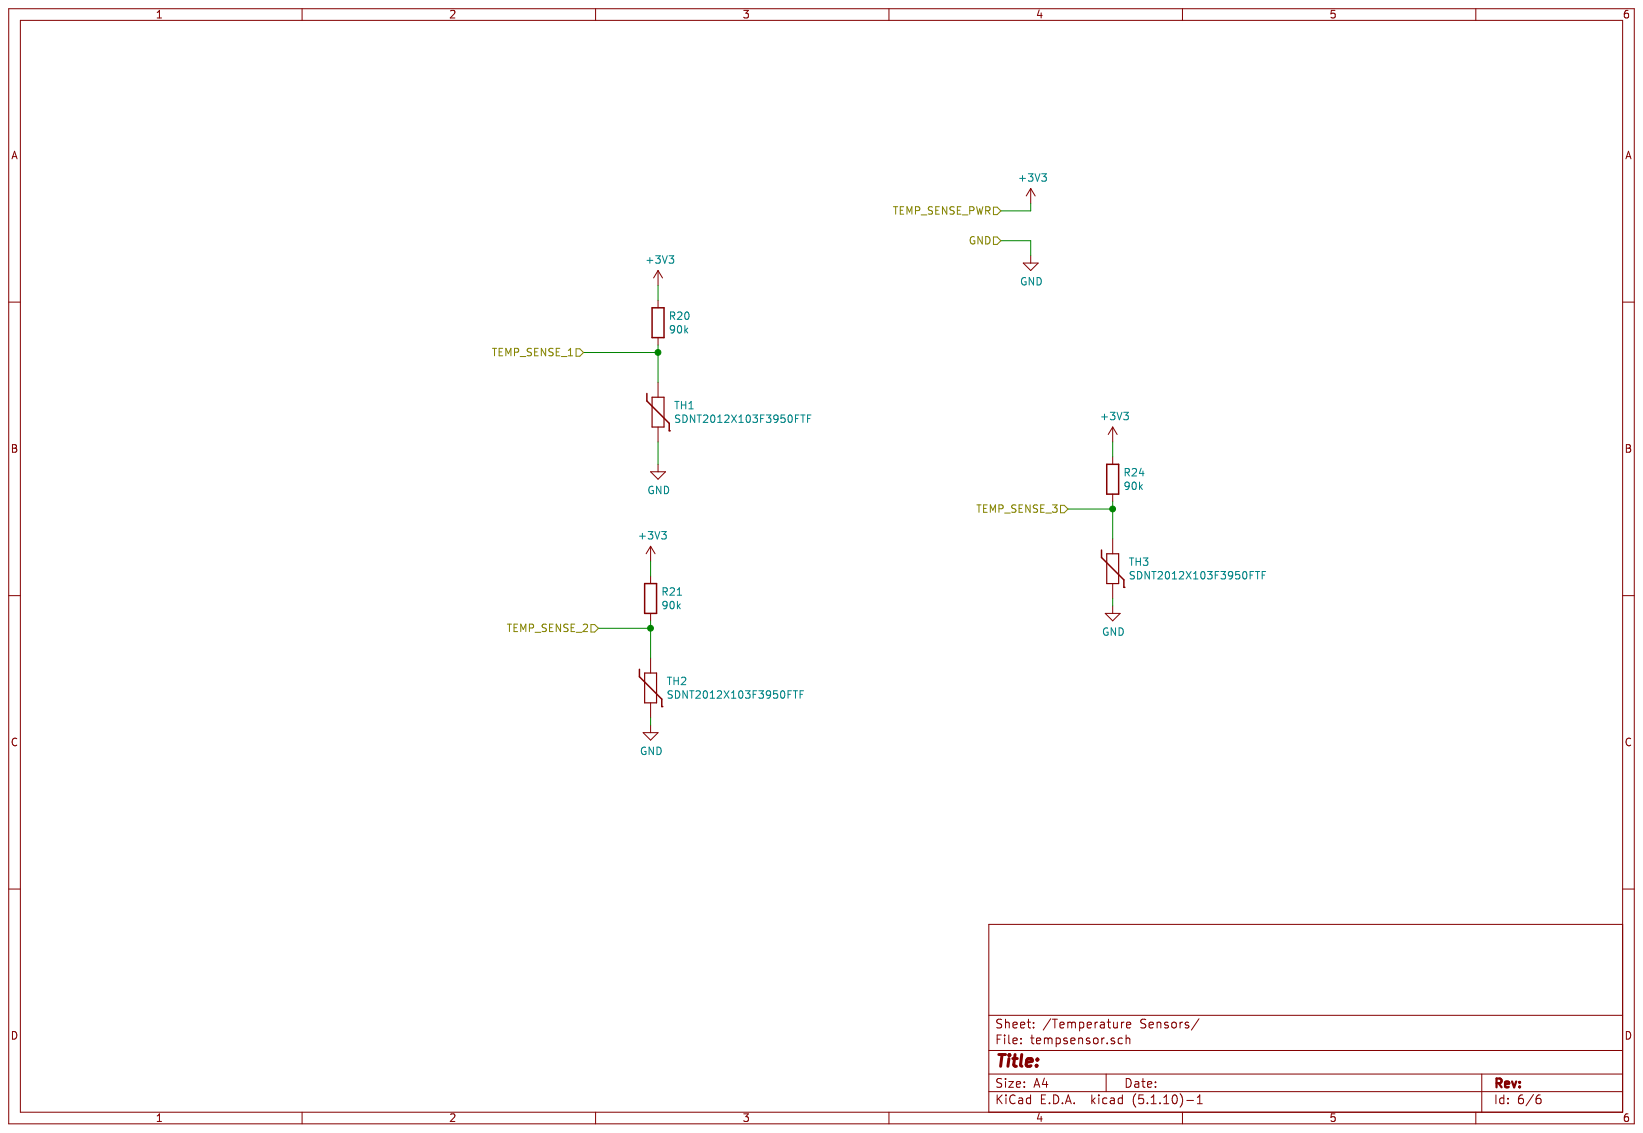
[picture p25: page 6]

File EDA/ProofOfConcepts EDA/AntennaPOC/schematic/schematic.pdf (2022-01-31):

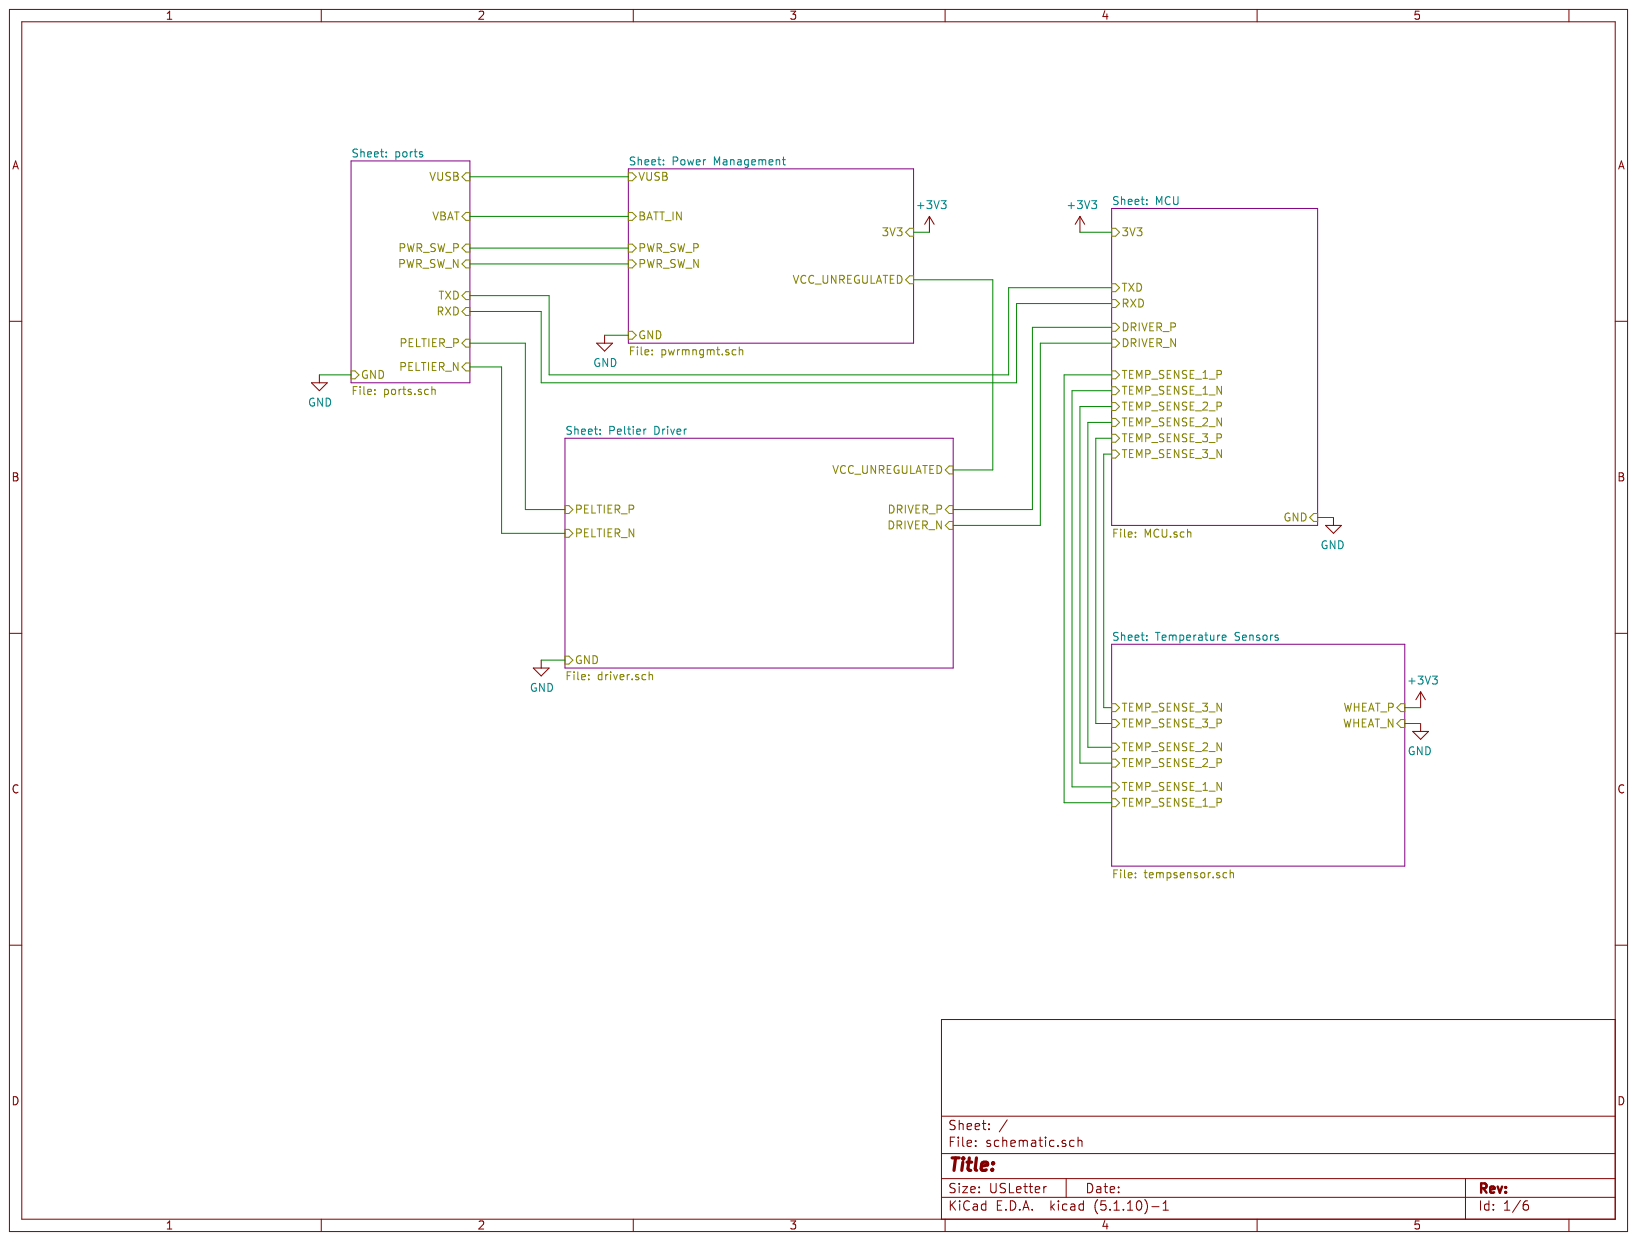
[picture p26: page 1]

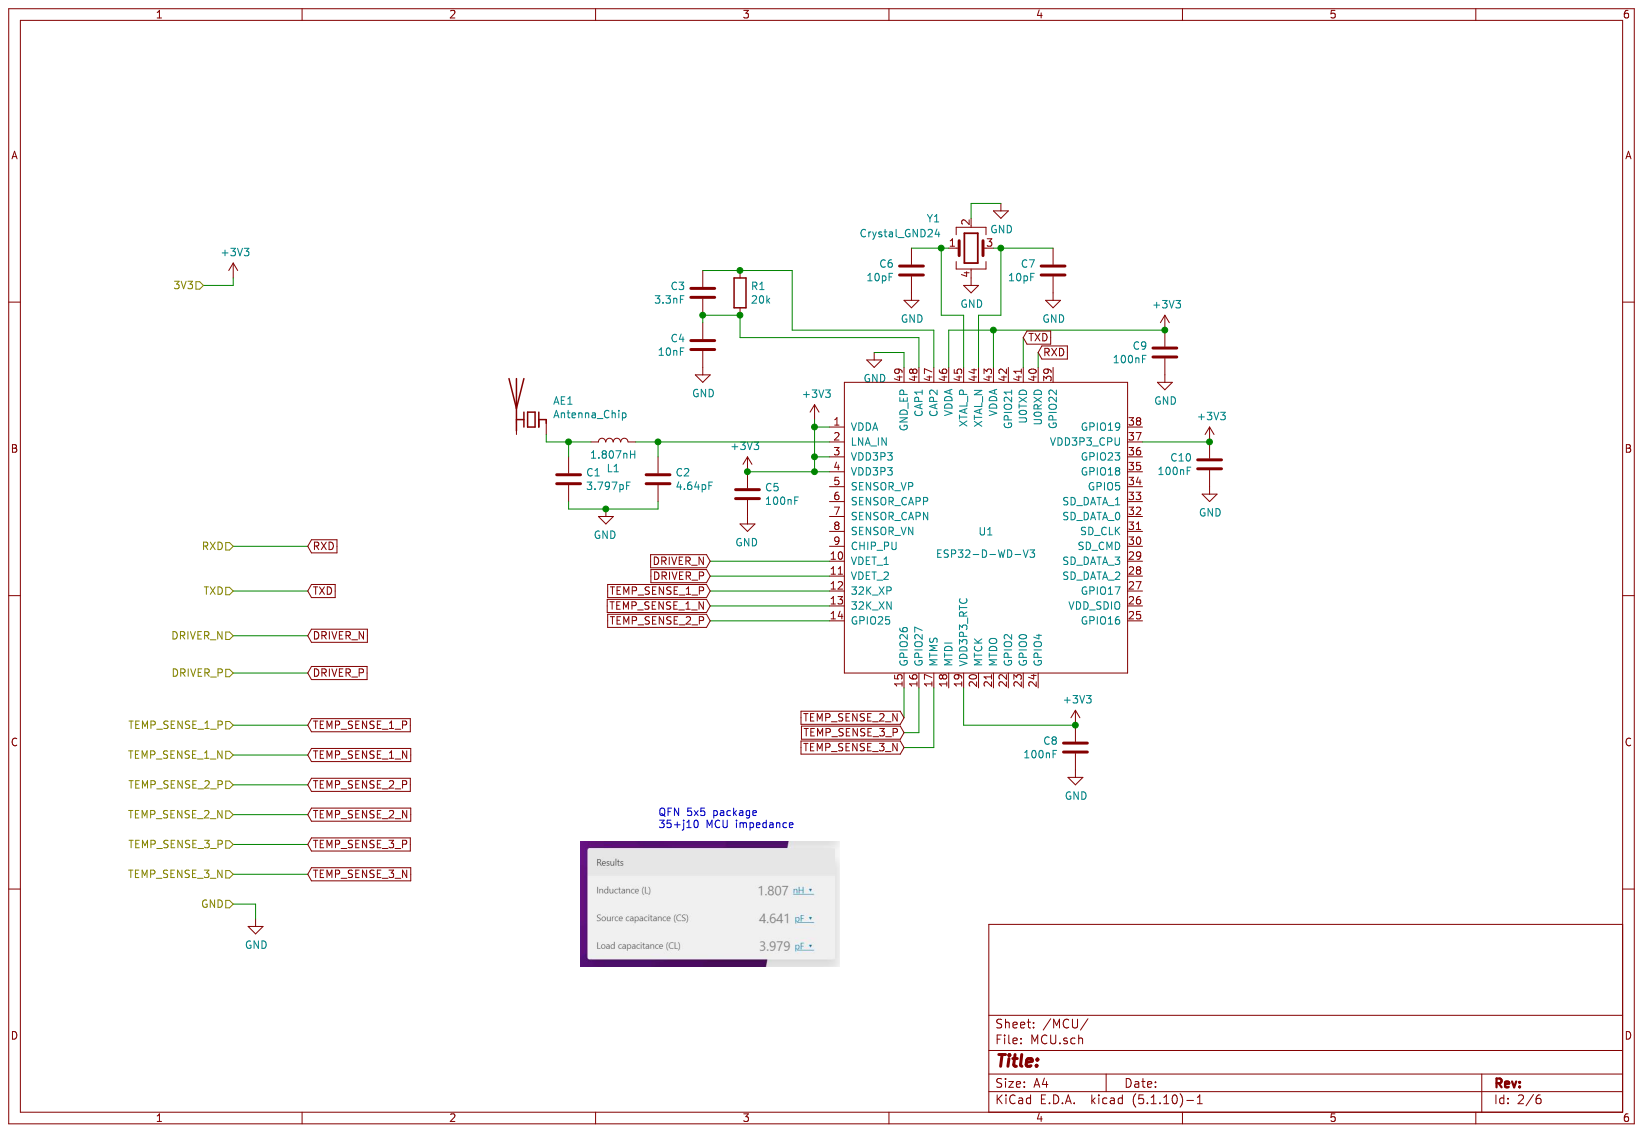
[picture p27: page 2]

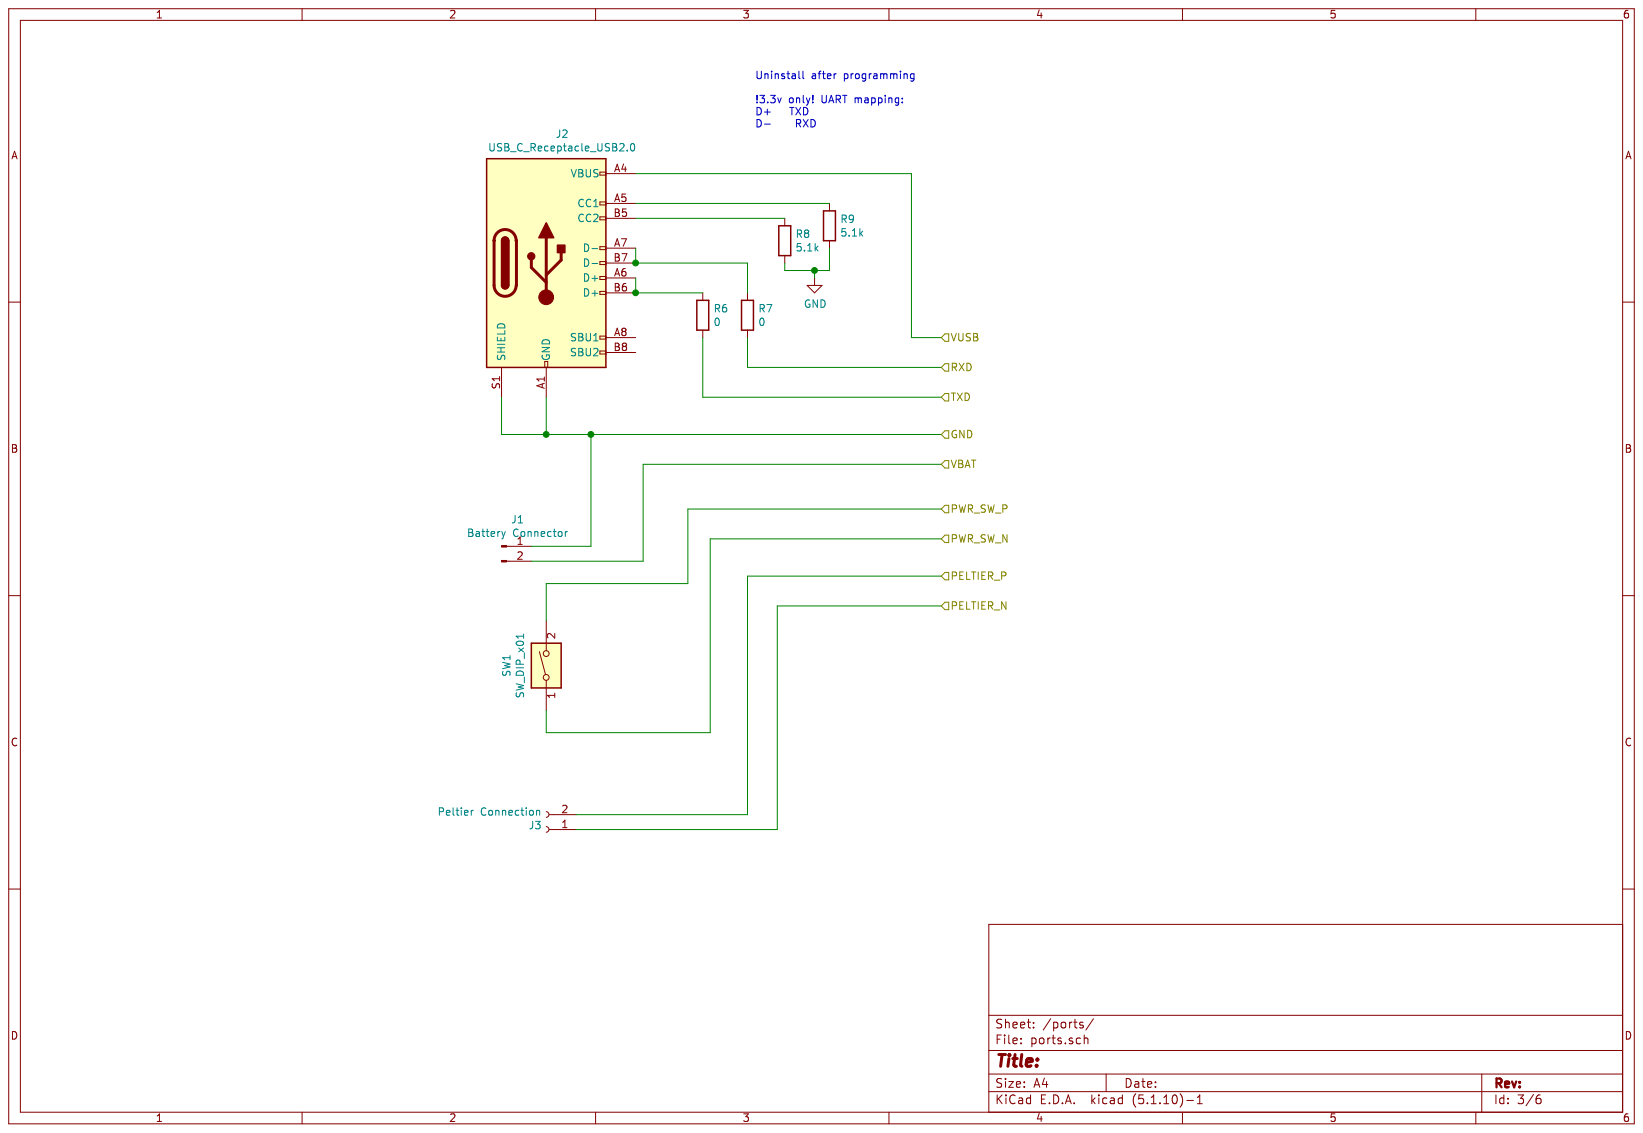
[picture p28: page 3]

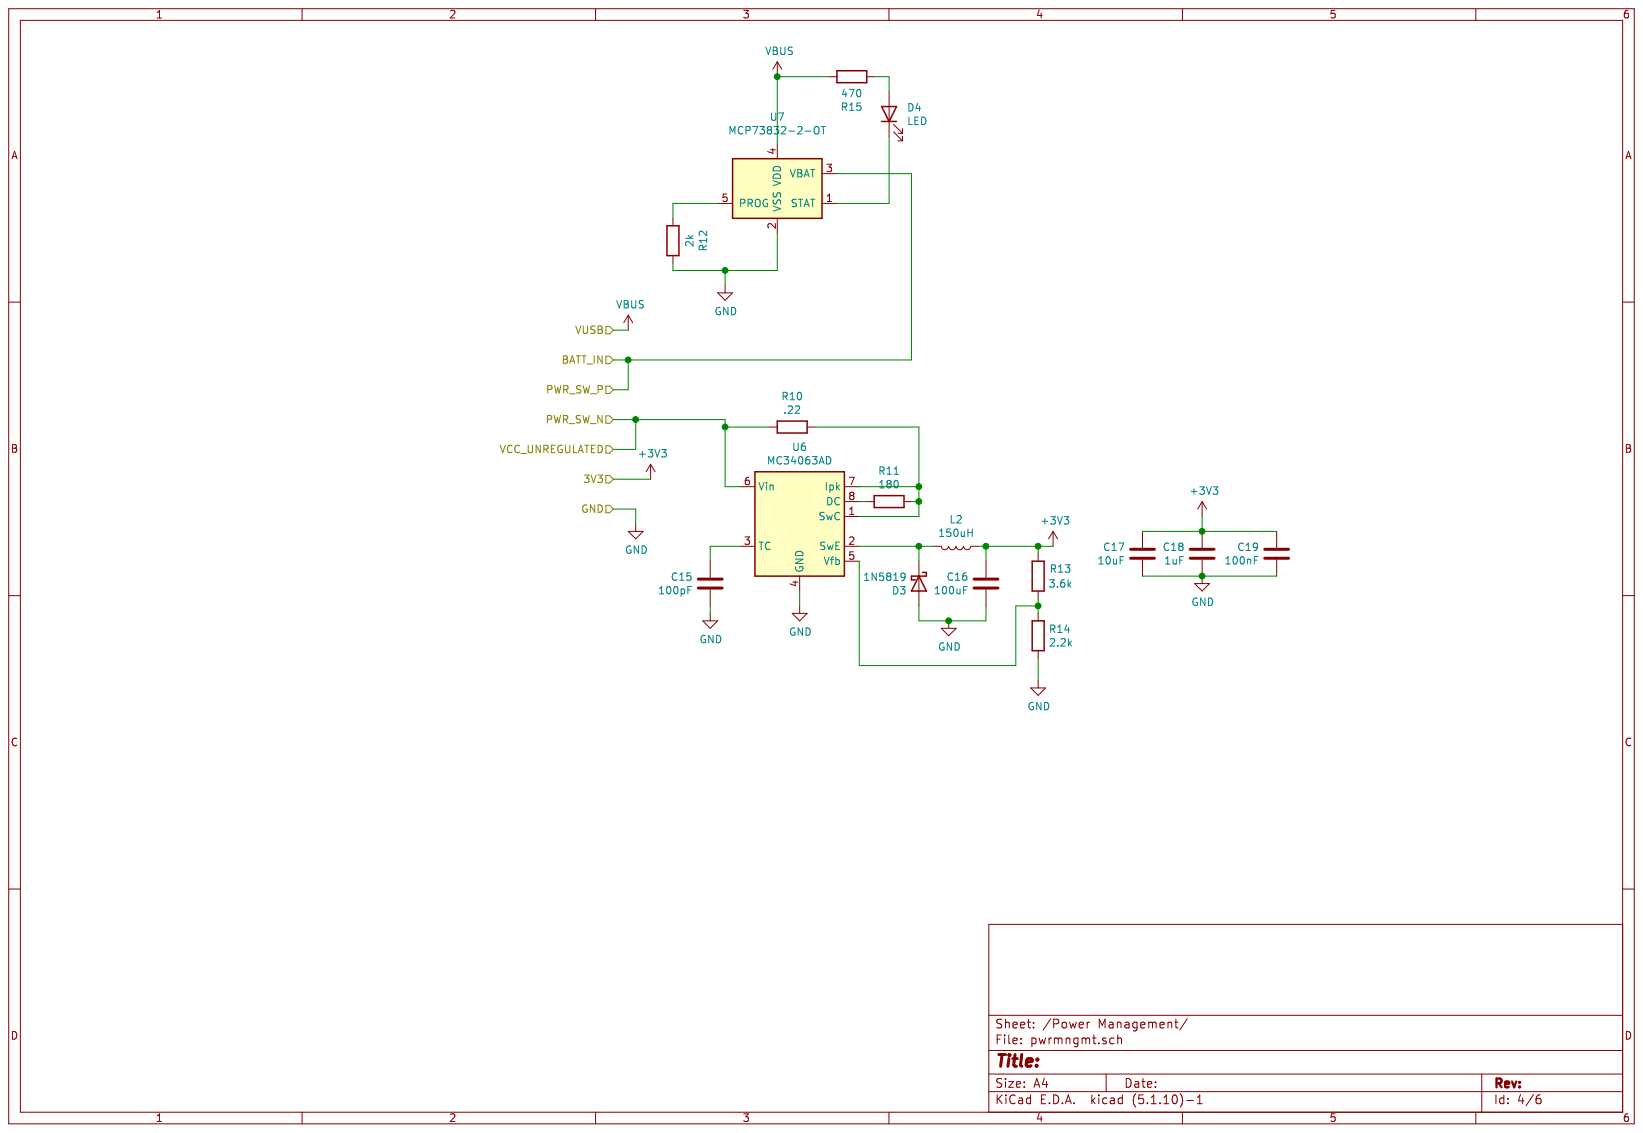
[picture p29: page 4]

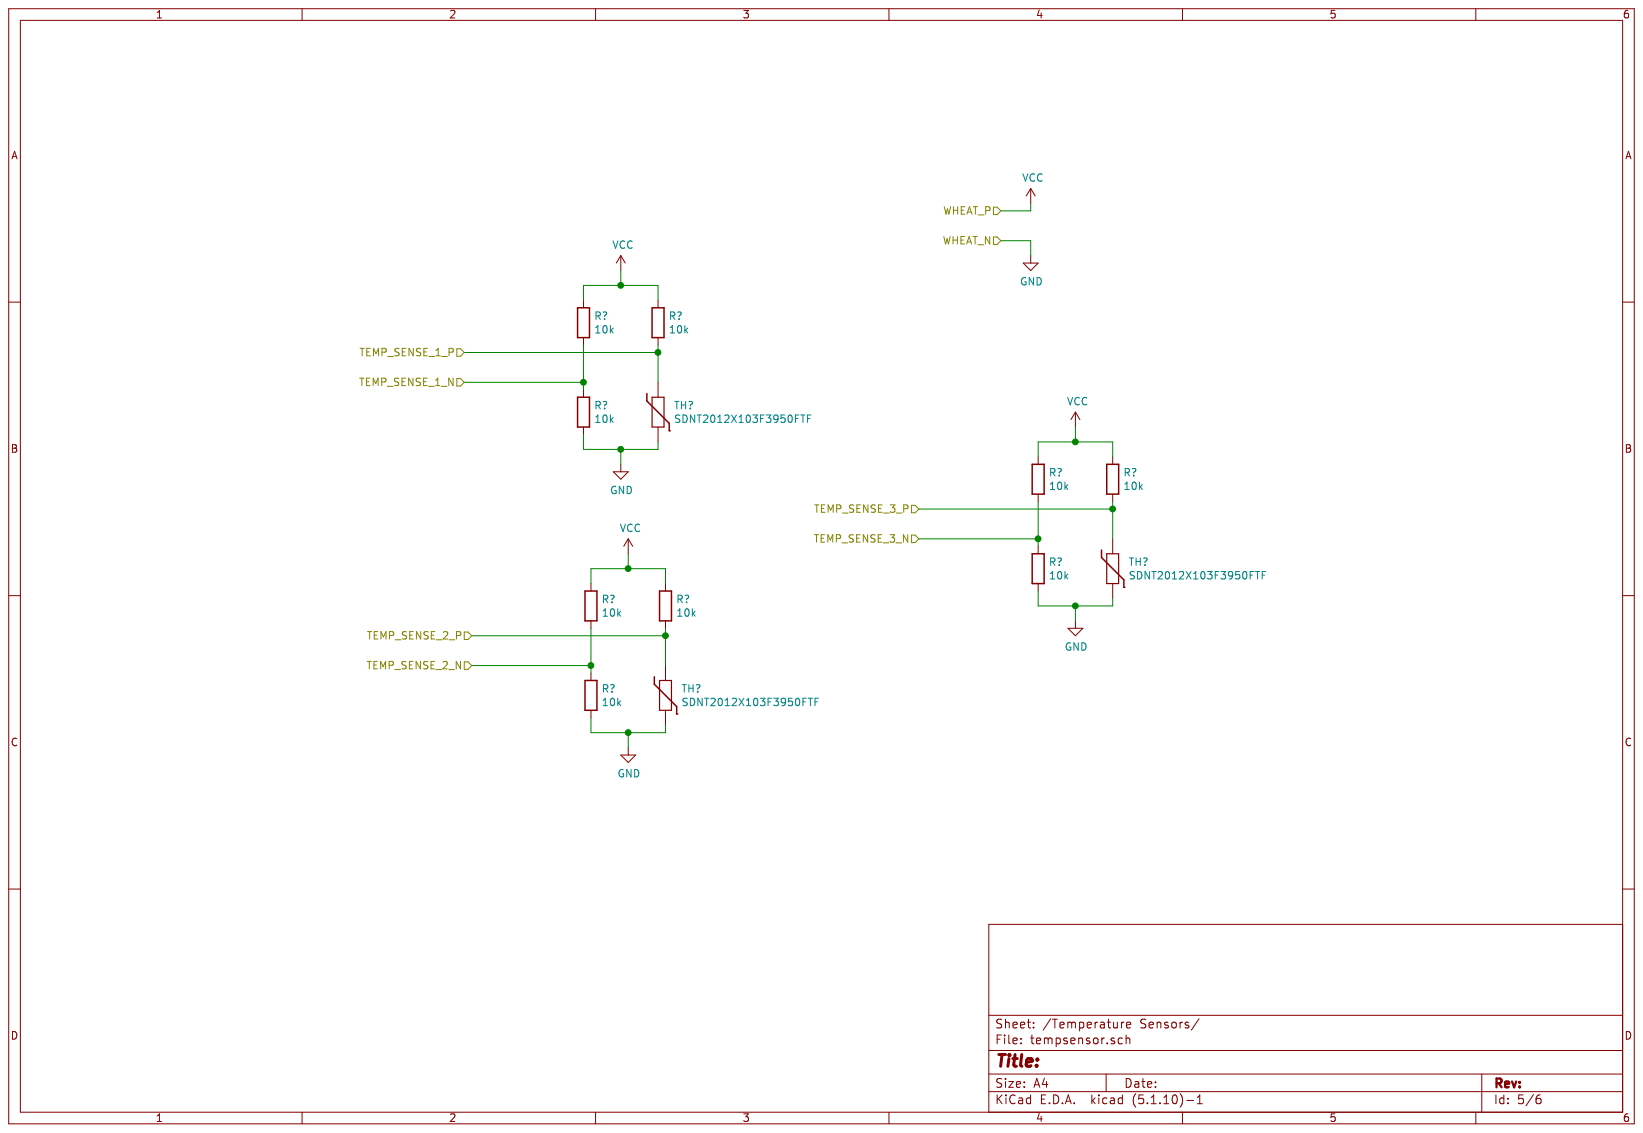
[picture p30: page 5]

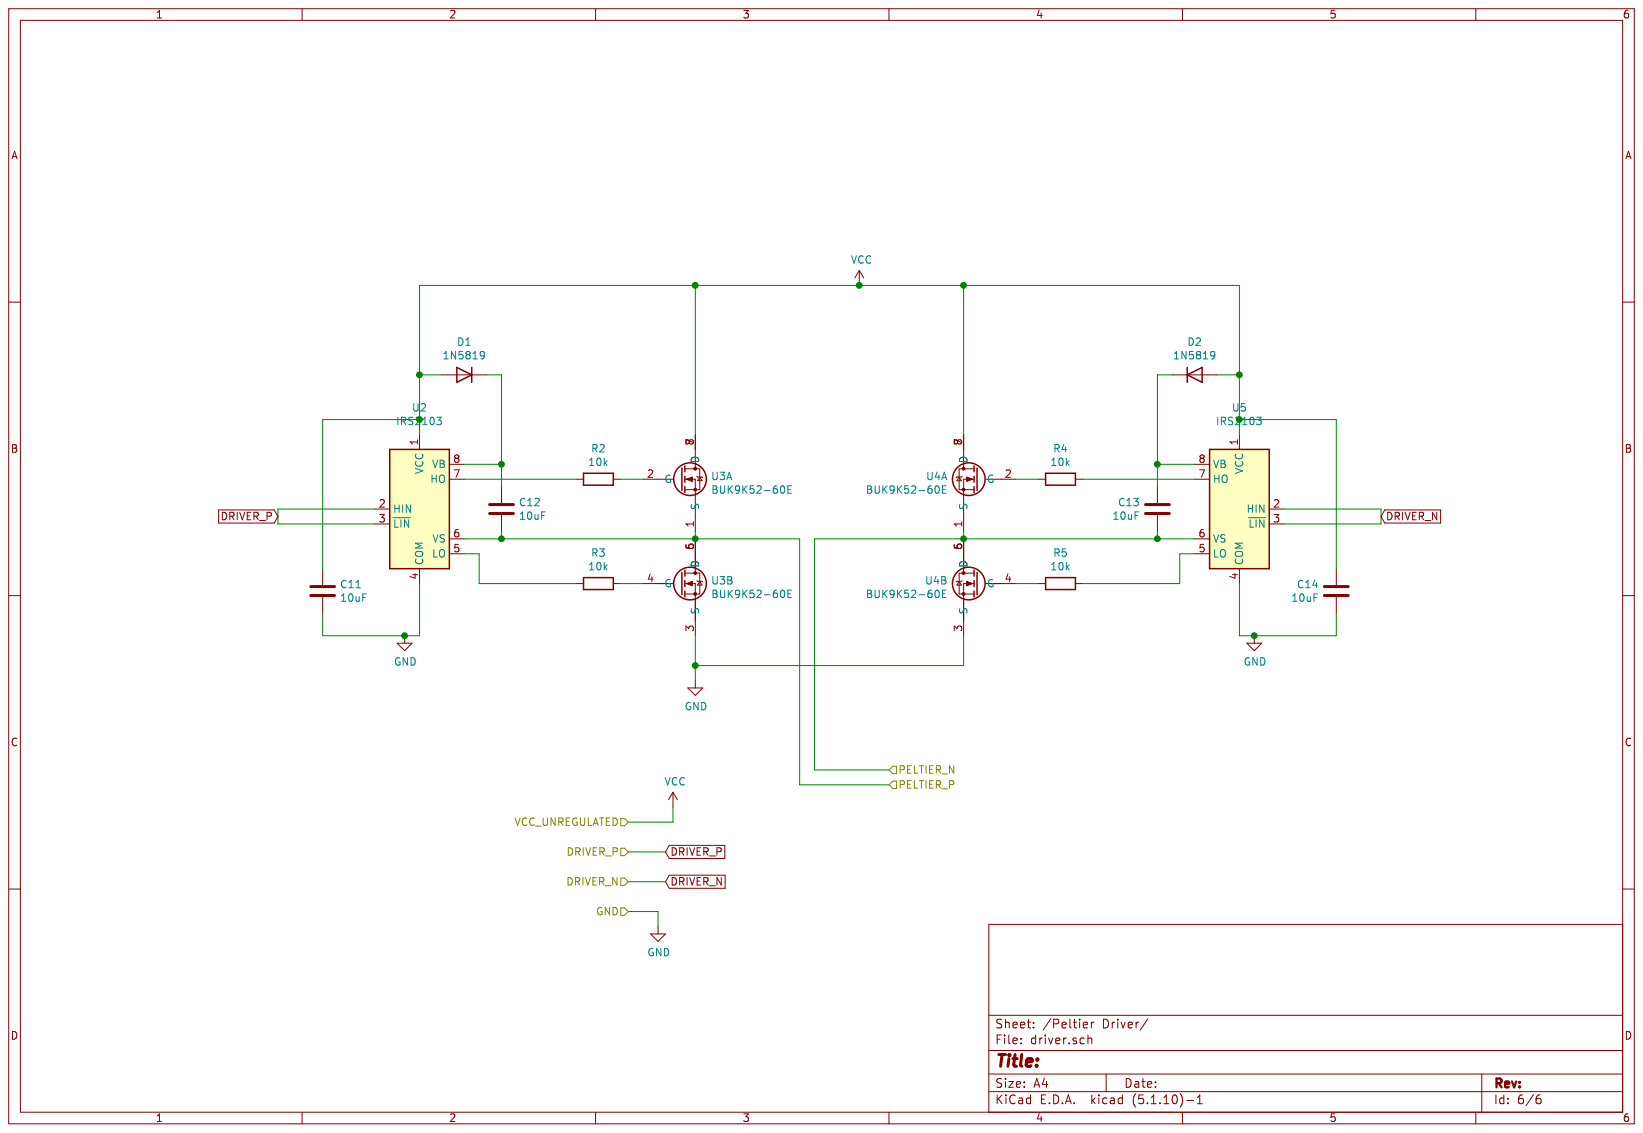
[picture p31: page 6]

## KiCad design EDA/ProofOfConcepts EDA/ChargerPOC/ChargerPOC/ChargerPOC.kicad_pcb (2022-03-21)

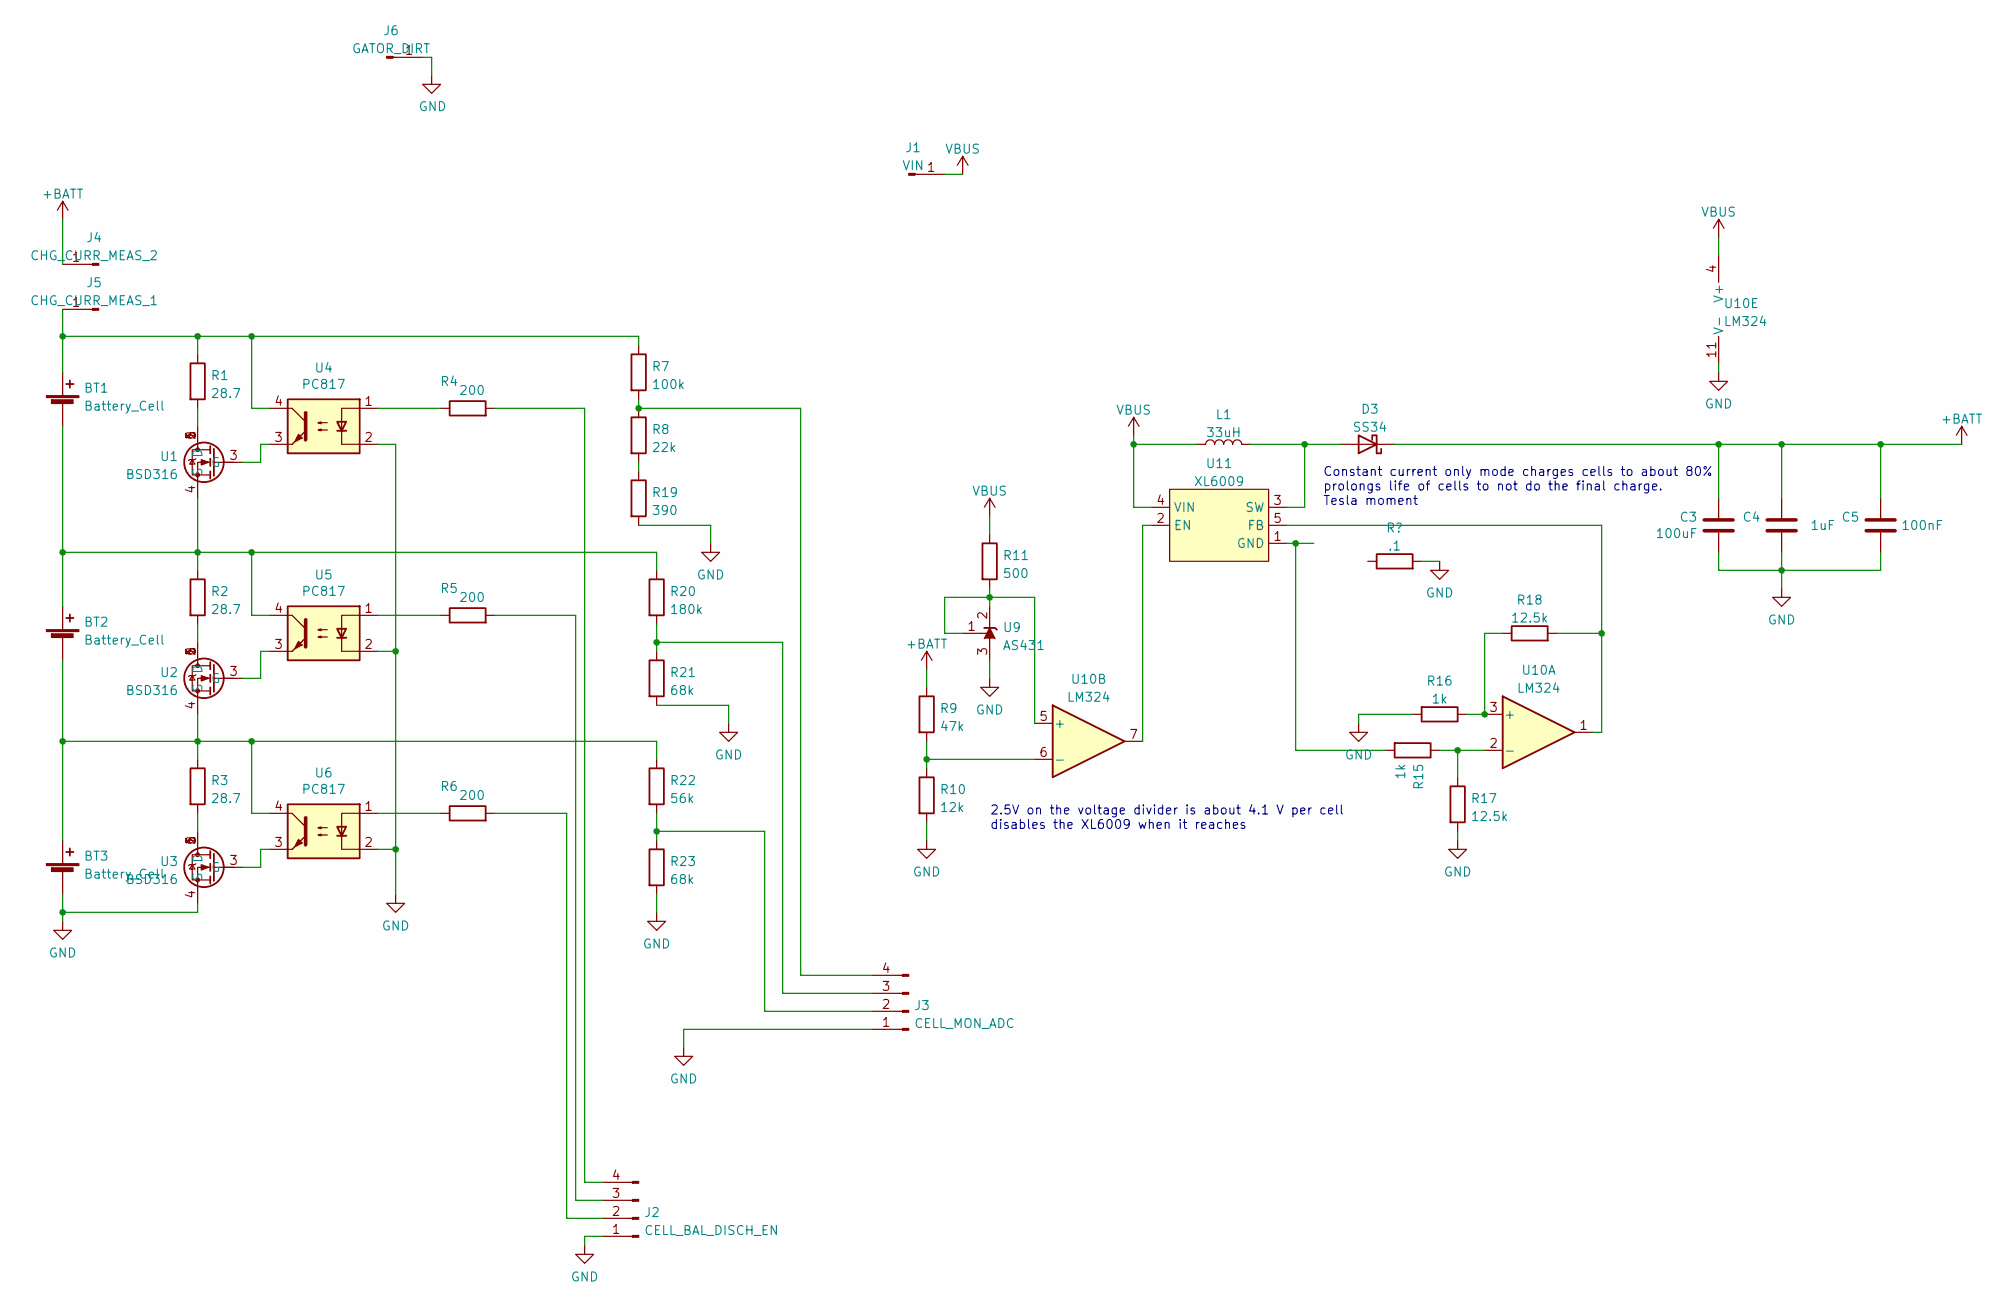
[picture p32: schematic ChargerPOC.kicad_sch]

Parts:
BT1, BT2, BT3: Battery_Cell; PinHeader_1x02_P2.54mm_Vertical
C3: 100uF; C_1210_3225Metric_Pad1.33x2.70mm_HandSolder
C4: 1uF; C_0805_2012Metric_Pad1.18x1.45mm_HandSolder
C5: 100nF; C_0805_2012Metric_Pad1.18x1.45mm_HandSolder
D3: SS34; D_SMA_Handsoldering
J1: VIN; GatorTestpoint
J2: CELL_BAL_DISCH_EN; PinHeader_1x04_P2.54mm_Vertical
J3: CELL_MON_ADC; PinHeader_1x04_P2.54mm_Vertical
J4: CHG_CURR_MEAS_2; GatorTestpoint
J5: CHG_CURR_MEAS_1; GatorTestpoint
J6: GATOR_DIRT; GatorTestpoint
L1: 33uH; L_10.4x10.4_H4.8
R1, R2, R3: 28.7; R_2512_6332Metric_Pad1.40x3.35mm_HandSolder
R4, R5, R6: 200; R_0805_2012Metric_Pad1.20x1.40mm_HandSolder
R7: 100k; R_0805_2012Metric_Pad1.20x1.40mm_HandSolder
R8: 22k; R_0805_2012Metric_Pad1.20x1.40mm_HandSolder
R9: 47k; R_0805_2012Metric_Pad1.20x1.40mm_HandSolder
R10: 12k; R_0805_2012Metric_Pad1.20x1.40mm_HandSolder
R11: 500; R_0805_2012Metric_Pad1.20x1.40mm_HandSolder
R15, R16: 1k; R_0805_2012Metric_Pad1.20x1.40mm_HandSolder
R17, R18: 12.5k; R_0805_2012Metric_Pad1.20x1.40mm_HandSolder
R19: 390; R_0805_2012Metric_Pad1.20x1.40mm_HandSolder
R20: 180k; R_0805_2012Metric_Pad1.20x1.40mm_HandSolder
R21, R23: 68k; R_0805_2012Metric_Pad1.20x1.40mm_HandSolder
R22: 56k; R_0805_2012Metric_Pad1.20x1.40mm_HandSolder
U1, U2, U3: BSD316; SOT-363_SC-70-6_Handsoldering
U4, U5, U6: PC817; SOP-4_3.8x4.1mm_P2.54mm
U9: AS431; SOT-23
U10: LM324; SOIC-14_3.9x8.7mm_P1.27mm
U11: XL6009; TO-263-5_TabPin3

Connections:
+BATT: C3.1, C4.1, C5.1, D3.1 (K), J4.1, R9.1
GND: BT3.2 (-), C3.2, C4.2, C5.2, J2.1, J3.1, J6.1, R10.2, R16.2, R17.2, R19.2, R21.2, R23.2, U3.4 (S), U4.2, U5.2, U6.2, U9.3, U10.11 (V-); also elsewhere on the board
unnamed: BT1.1 (+), J5.1, R1.1, R7.1, U4.4
unnamed: BT1.2 (-), BT2.1 (+), R2.1, R20.1, U1.4 (S), U5.4
unnamed: BT2.2 (-), BT3.1 (+), R3.1, R22.1, U2.4 (S), U6.4
unnamed: D3.2 (A), L1.2, U11.3 (SW)
unnamed: J2.2, R6.2
unnamed: J2.3, R5.2
unnamed: J2.4, R4.2
unnamed: J3.2, R22.2, R23.1
unnamed: J3.3, R20.2, R21.1
unnamed: J3.4, R7.2, R8.1
unnamed: R1.2, U1.1 (D), U1.2 (D), U1.5 (D), U1.6 (D)
unnamed: R2.2, U2.1 (D), U2.2 (D), U2.5 (D), U2.6 (D)
unnamed: R3.2, U3.1 (D), U3.2 (D), U3.5 (D), U3.6 (D)
unnamed: R4.1, U4.1
unnamed: R5.1, U5.1
unnamed: R6.1, U6.1
unnamed: R9.2, R10.1, U10.6 (-)
unnamed: R11.2, U9.1, U9.2, U10.5 (+)
unnamed 20: R15.2, U11.1 (GND); also elsewhere on the board
unnamed: R15.1, R17.1, U10.2 (-)
unnamed: R16.1, R18.1, U10.3 (+)
unnamed: R18.2, U10.1, U11.5 (FB)
unnamed: R8.2, R19.1
unnamed: U1.3 (G), U4.3
unnamed: U2.3 (G), U5.3
unnamed: U3.3 (G), U6.3
unnamed: U10.7, U11.2 (EN)
VBUS: J1.1, L1.1, R11.1, U10.4 (V+), U11.4 (VIN)

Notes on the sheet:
2.5V on the voltage divider is about 4.1 V per cell disables the XL6009 when it reaches
Constant current only mode charges cells to about 80% prolongs life of cells to not do the final charge. Tesla moment

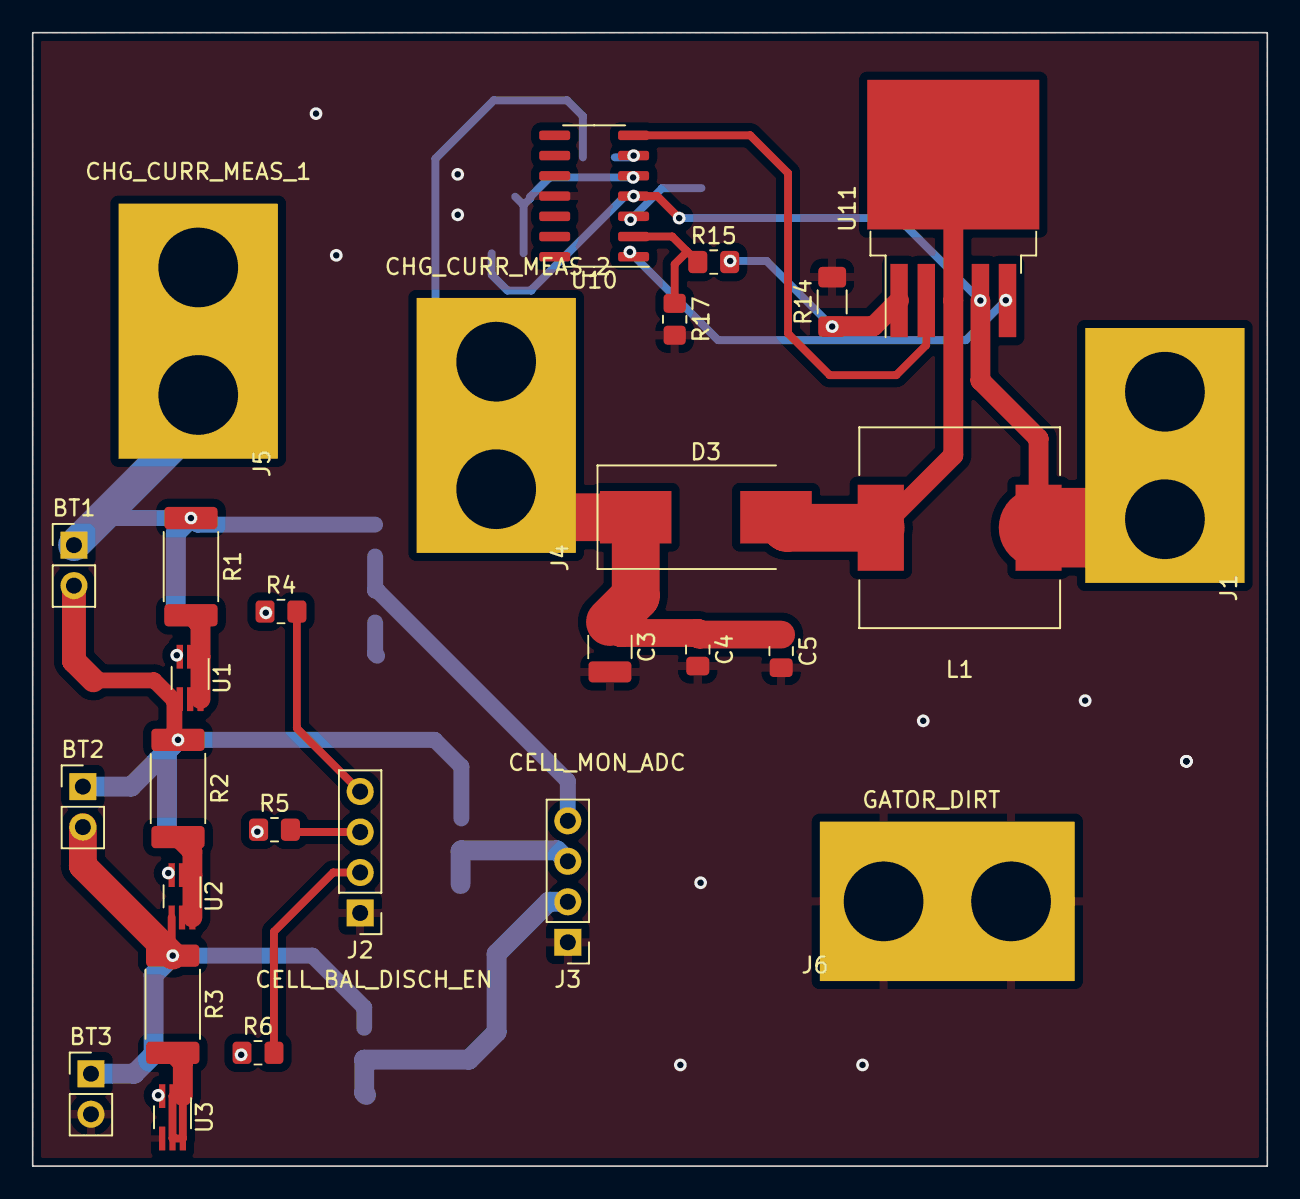
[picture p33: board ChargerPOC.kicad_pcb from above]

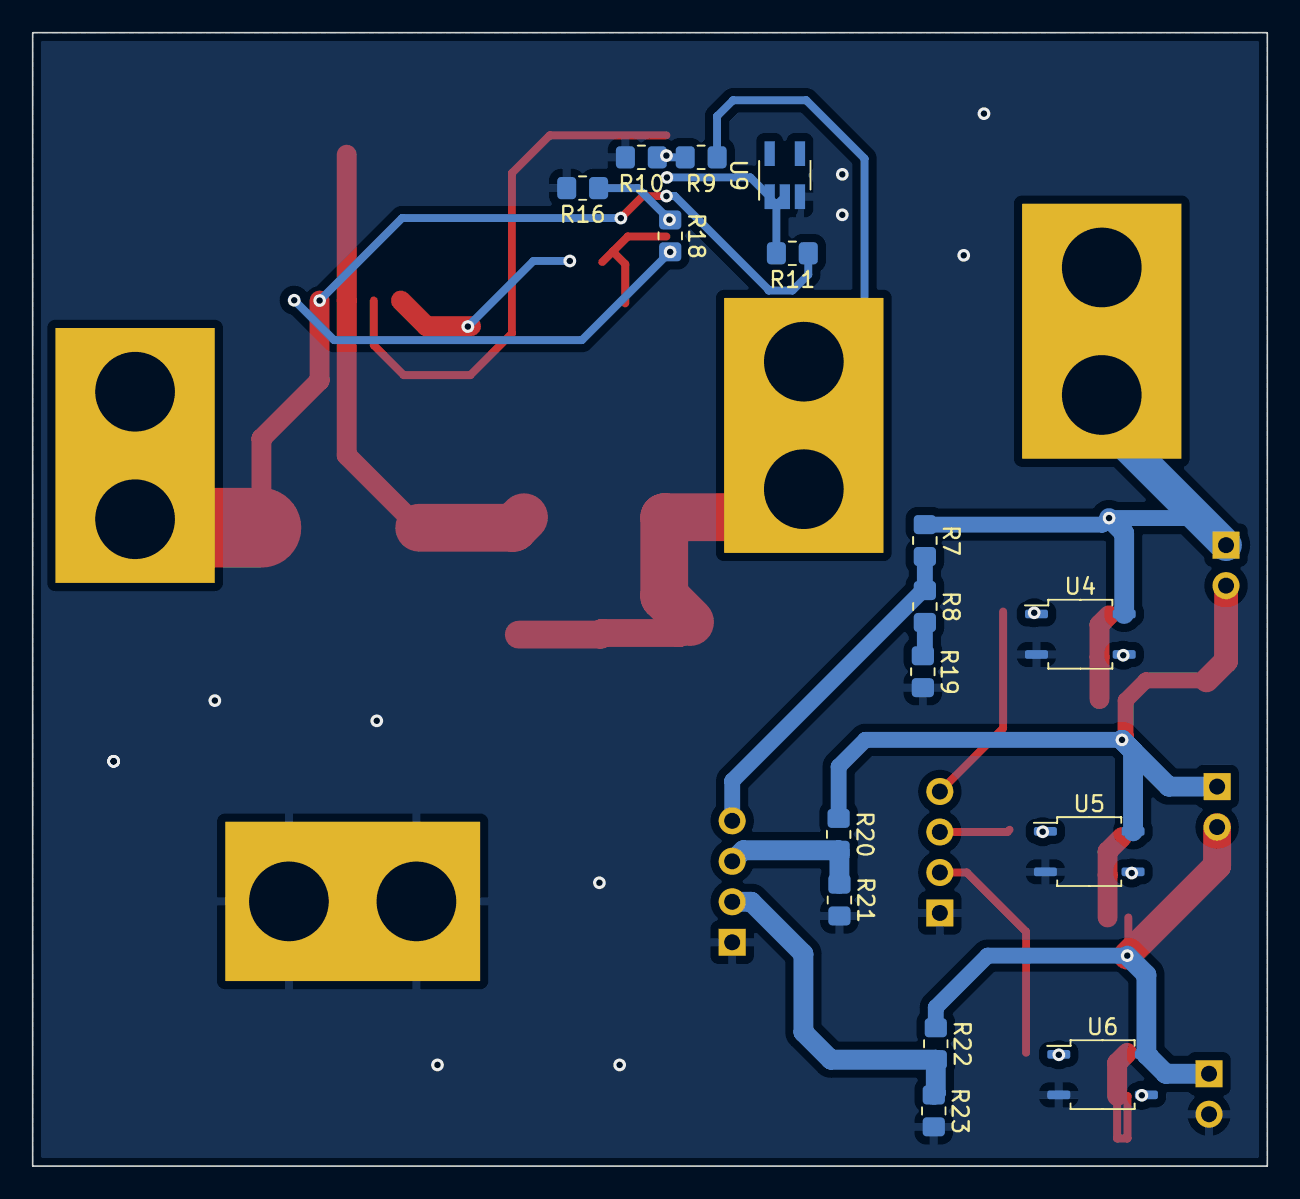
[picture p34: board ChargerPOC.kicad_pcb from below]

Board: 2 copper layers, 77.5 x 71.1 mm, 44 parts (16 on the bottom side), 30 nets.

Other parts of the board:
R14: .1; R_1206_3216Metric_Pad1.30x1.75mm_HandSolder

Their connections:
GND: R14.2; also elsewhere on the board
unnamed 20: R14.1; also elsewhere on the board

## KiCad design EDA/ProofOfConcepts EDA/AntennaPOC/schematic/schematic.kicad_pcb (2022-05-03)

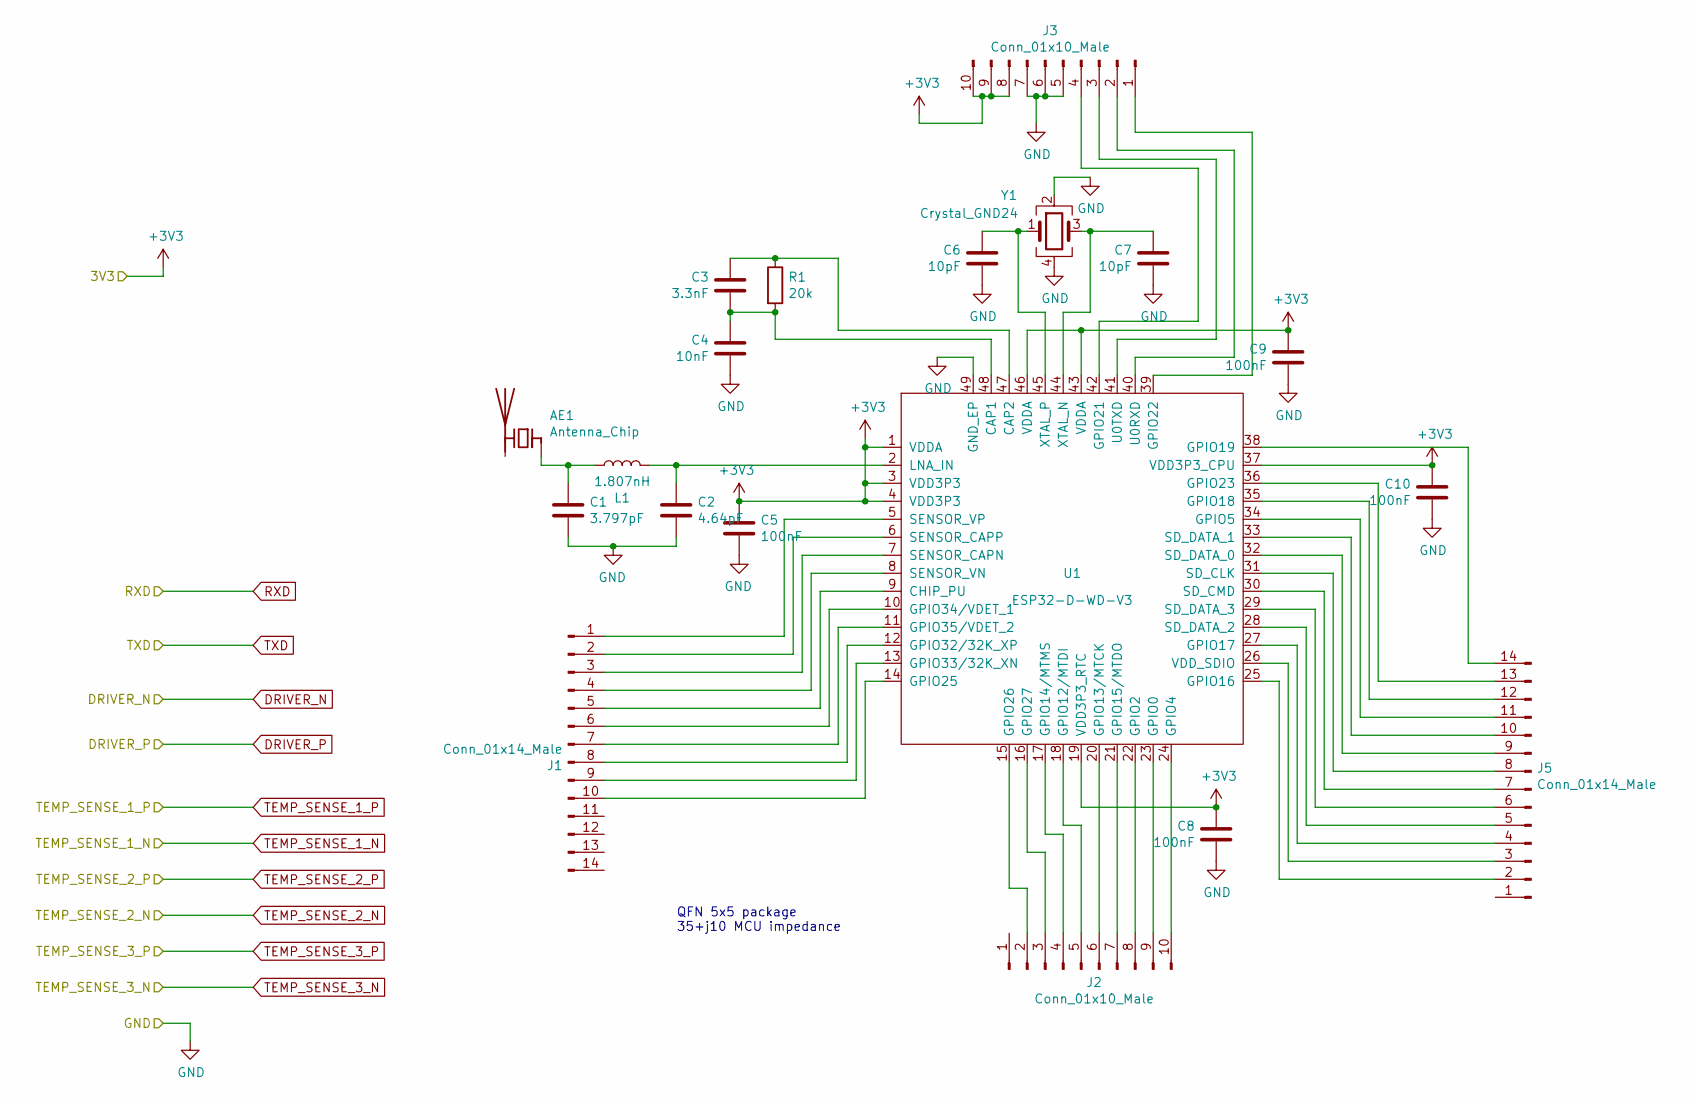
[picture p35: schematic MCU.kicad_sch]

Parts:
AE1: Antenna_Chip; Johanson_2450AT18x100
C1: 3.797pF; C_0805_2012Metric_Pad1.18x1.45mm_HandSolder
C2: 4.64pF; C_0805_2012Metric_Pad1.18x1.45mm_HandSolder
C3: 3.3nF; C_0805_2012Metric_Pad1.18x1.45mm_HandSolder
C4: 10nF; C_0805_2012Metric_Pad1.18x1.45mm_HandSolder
C5, C8, C9, C10: 100nF; C_0805_2012Metric_Pad1.18x1.45mm_HandSolder
C6, C7: 10pF; C_0805_2012Metric_Pad1.18x1.45mm_HandSolder
J1, J5: Conn_01x14_Male; PinHeader_1x14_P2.54mm_Vertical
J2, J3: Conn_01x10_Male; PinHeader_1x10_P2.54mm_Vertical
L1: 1.807nH; L_0805_2012Metric_Pad1.15x1.40mm_HandSolder
R1: 20k; R_0805_2012Metric_Pad1.20x1.40mm_HandSolder
U1: ESP32-D-WD-V3; QFN-48-1EP_5x5mm_P0.35mm_EP3.7x3.7mm_ThermalVias
Y1: Crystal_GND24; Crystal_SMD_SeikoEpson_FA238-4Pin_3.2x2.5mm_HandSoldering

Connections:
unnamed: AE1.1 (FEED), C1.1, L1.1
unnamed: C2.1, L1.2, U1.2 (LNA_IN)
unnamed: C3.1, R1.1, U1.47 (CAP2)
unnamed: C3.2, C4.1, R1.2, U1.48 (CAP1)
unnamed: C6.1, U1.45 (XTAL_P), Y1.1
unnamed: C7.1, U1.44 (XTAL_N), Y1.3
unnamed: J1.1, U1.5 (SENSOR_VP)
unnamed: J1.2, U1.6 (SENSOR_CAPP)
unnamed: J1.3, U1.7 (SENSOR_CAPN)
unnamed: J1.4, U1.8 (SENSOR_VN)
unnamed: J1.5, U1.9 (CHIP_PU)
unnamed: J1.6, U1.10 (GPIO34/VDET_1)
unnamed: J1.7, U1.11 (GPIO35/VDET_2)
unnamed: J1.8, U1.12 (GPIO32/32K_XP)
unnamed: J1.9, U1.13 (GPIO33/32K_XN)
unnamed: J1.10, U1.14 (GPIO25)
unnamed: J2.2, U1.15 (GPIO26)
unnamed: J2.3, U1.16 (GPIO27)
unnamed: J2.4, U1.17 (GPIO14/MTMS)
unnamed: J2.5, U1.18 (GPIO12/MTDI)
unnamed: J2.6, U1.20 (GPIO13/MTCK)
unnamed: J2.7, U1.21 (GPIO15/MTDO)
unnamed: J2.8, U1.22 (GPIO2)
unnamed: J3.1, U1.39 (GPIO22)
unnamed: J3.2, U1.40 (U0RXD)
unnamed: J3.3, U1.41 (U0TXD)
unnamed: J3.4, U1.42 (GPIO21)
unnamed: J5.2, U1.25 (GPIO16)
unnamed: J5.3, U1.26 (VDD_SDIO)
unnamed: J5.4, U1.27 (GPIO17)
unnamed: J5.5, U1.28 (SD_DATA_2)
unnamed: J5.6, U1.29 (SD_DATA_3)
unnamed: J5.7, U1.30 (SD_CMD)
unnamed: J5.8, U1.31 (SD_CLK)
unnamed: J5.9, U1.32 (SD_DATA_0)
unnamed: J5.10, U1.33 (SD_DATA_1)
unnamed: J5.11, U1.34 (GPIO5)
unnamed: J5.12, U1.35 (GPIO18)
unnamed: J5.13, U1.36 (GPIO23)
unnamed: J5.14, U1.38 (GPIO19)
unnamed: J2.9, U1.23 (GPIO0)
unnamed: J2.10, U1.24 (GPIO4)

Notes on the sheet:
QFN 5x5 package 35+j10 MCU impedance

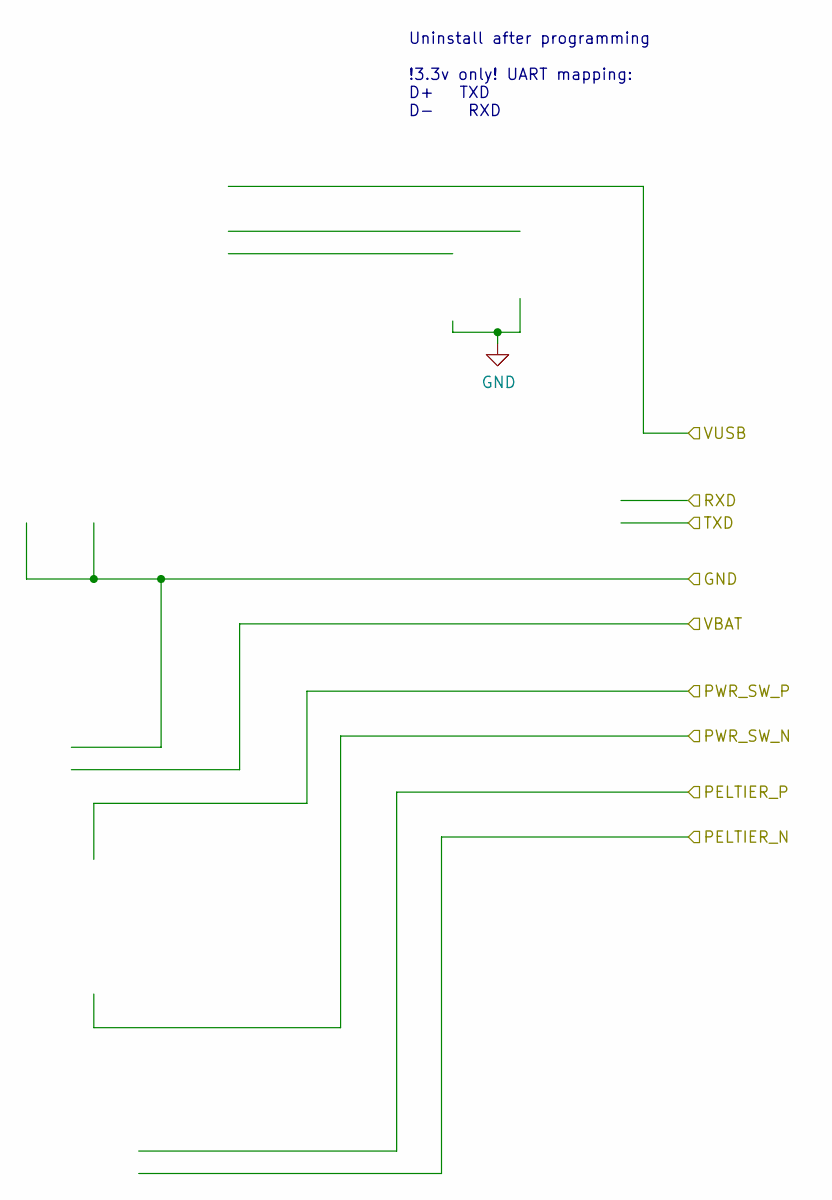
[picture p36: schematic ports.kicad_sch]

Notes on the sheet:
Uninstall after programming !3.3v only! UART mapping: D+ TXD D- RXD

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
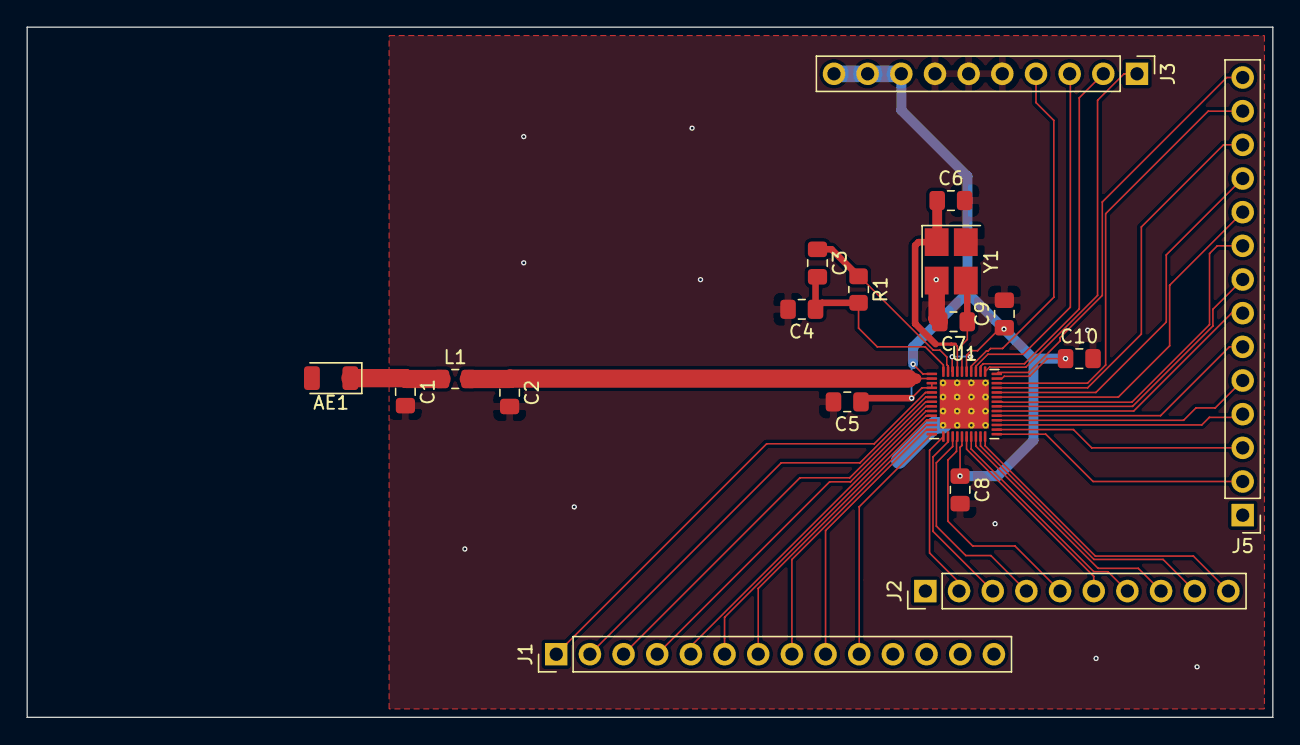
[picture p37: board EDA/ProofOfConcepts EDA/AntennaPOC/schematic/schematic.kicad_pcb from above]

Board: 2 copper layers, 94.0 x 52.1 mm, 19 parts (0 on the bottom side), 44 nets.

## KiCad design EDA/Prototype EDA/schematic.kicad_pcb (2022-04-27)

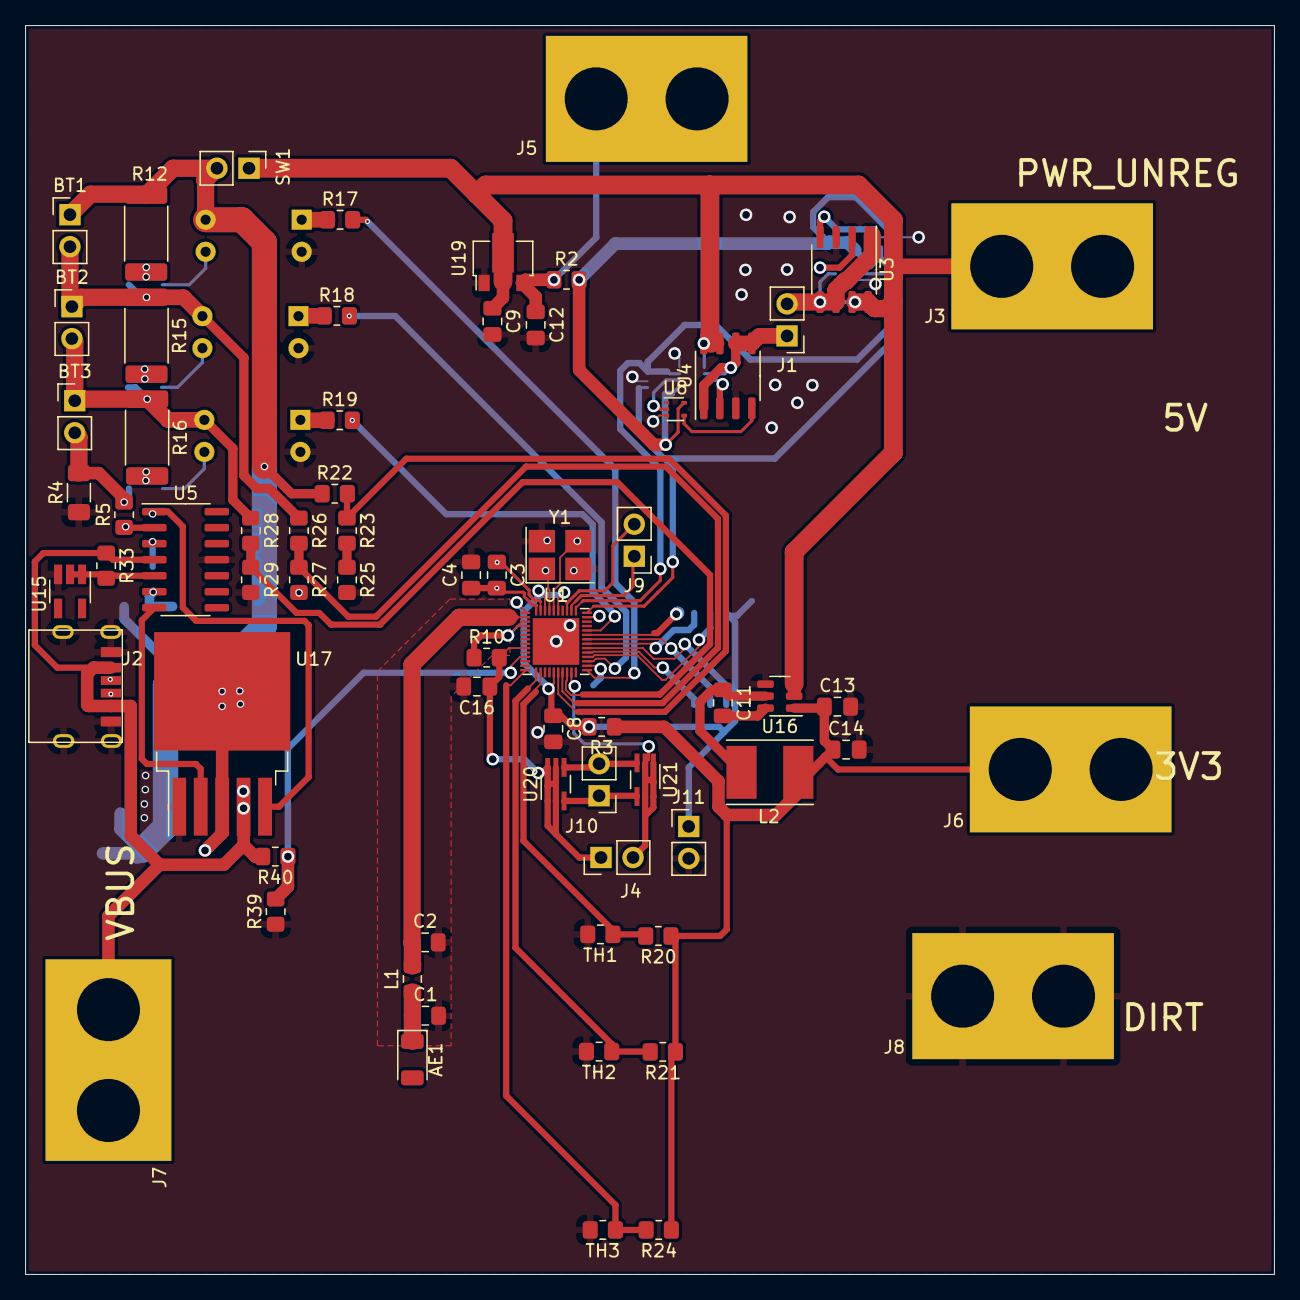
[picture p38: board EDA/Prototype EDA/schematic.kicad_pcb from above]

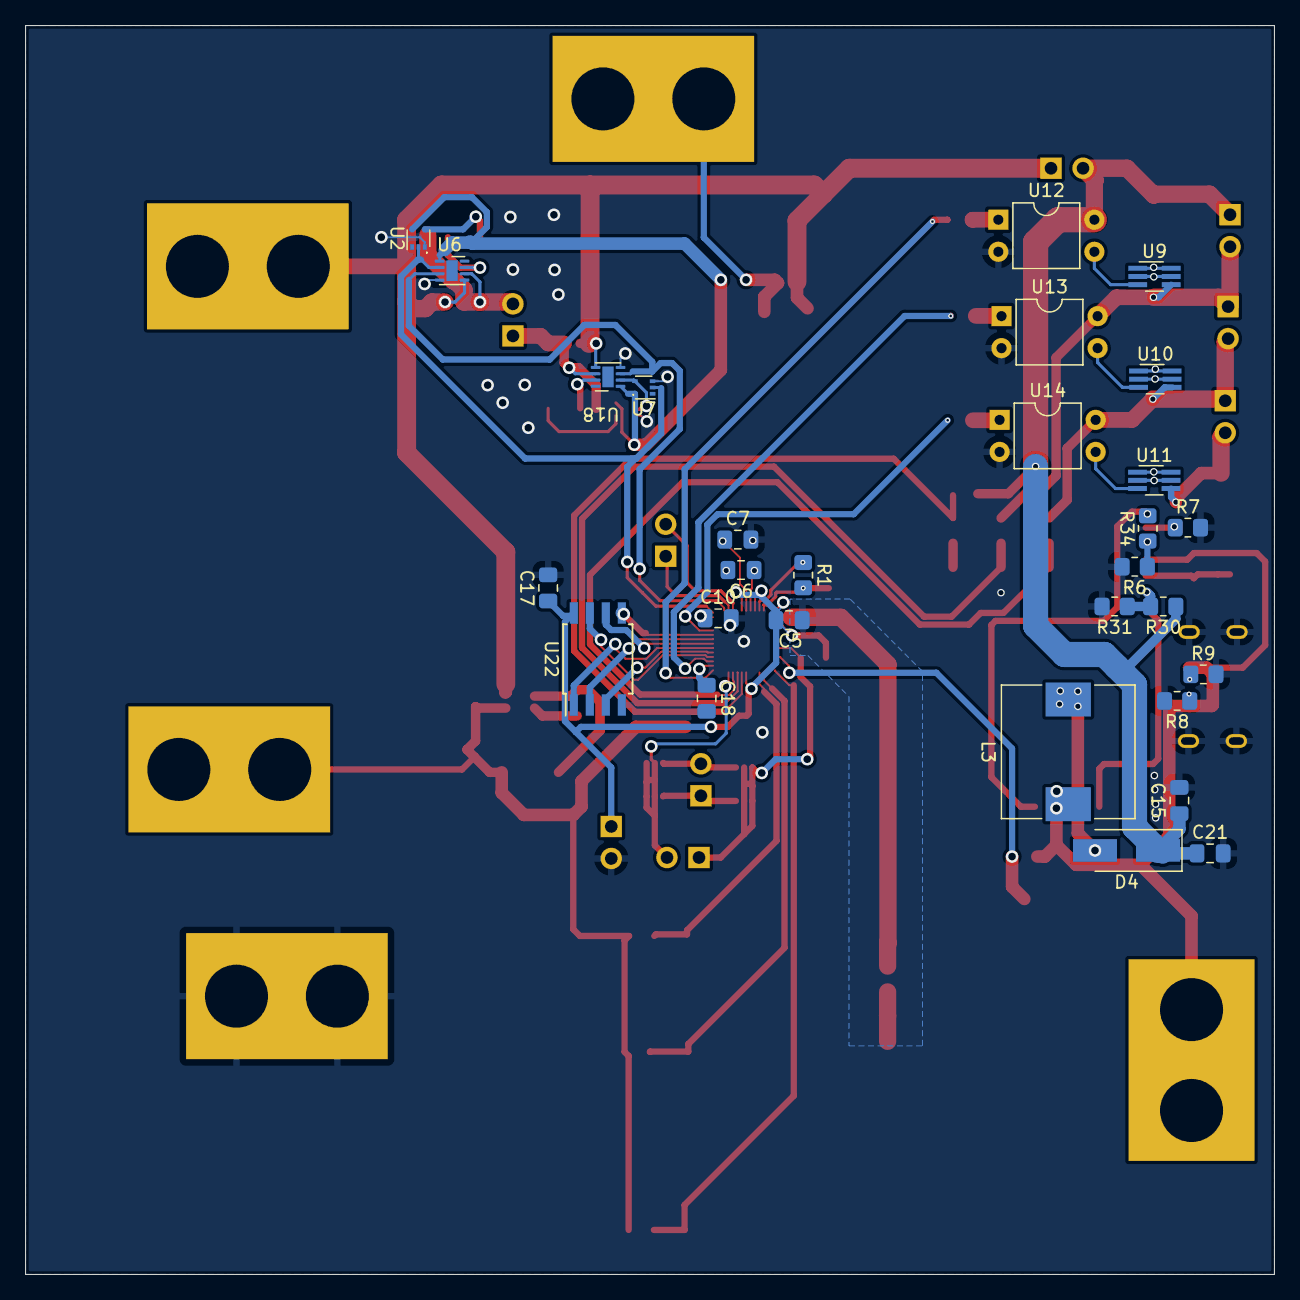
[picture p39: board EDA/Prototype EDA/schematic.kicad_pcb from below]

Board: 2 copper layers, 99.1 x 99.1 mm, 97 parts (29 on the bottom side), 71 nets.

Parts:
AE1: Antenna_Chip; Johanson_2450AT18x100
BT1, BT2, BT3: Battery_Cell; PinHeader_1x02_P2.54mm_Vertical
C1: 3.797pF; C_0805_2012Metric_Pad1.18x1.45mm_HandSolder
C2: 4.64pF; C_0805_2012Metric_Pad1.18x1.45mm_HandSolder
C3: 3.3nF; C_0805_2012Metric_Pad1.18x1.45mm_HandSolder
C4: 10nF; C_0805_2012Metric_Pad1.18x1.45mm_HandSolder
C5, C8, C10, C11, C16, C17, C21: 100nF; C_0805_2012Metric_Pad1.18x1.45mm_HandSolder
C6, C7: 10pF; C_0805_2012Metric_Pad1.18x1.45mm_HandSolder
C9, C12, C15: 10uF; C_0805_2012Metric_Pad1.18x1.45mm_HandSolder
C13, C14: 22uF; C_0805_2012Metric_Pad1.18x1.45mm_HandSolder
C18: 1uF; C_0805_2012Metric_Pad1.18x1.45mm_HandSolder
D4: SS34; D_SMA_Handsoldering
J1: Peltier Connection; PinHeader_1x02_P2.54mm_Vertical
J2: USB_C_Receptacle_USB2.0; USB4125-GF-A
J3, J5, J6, J7, J8: Conn_01x01_Male; GatorTestpoint
J4, J9, J10, J11: PROG_PORT; PinHeader_1x02_P2.54mm_Vertical
L1: 1.807nH; L_0805_2012Metric_Pad1.15x1.40mm_HandSolder
L2: 3.3uH NRS5024T3R3NMGJ; L_Taiyo-Yuden_NR-50xx_HandSoldering
L3: 33uH; L_10.4x10.4_H4.8
R1, R10: 20k; R_0805_2012Metric_Pad1.20x1.40mm_HandSolder
R2, R3: 0; R_0805_2012Metric_Pad1.20x1.40mm_HandSolder
R4: .1; R_1206_3216Metric_Pad1.30x1.75mm_HandSolder
R5, R6: 1k; R_0805_2012Metric_Pad1.20x1.40mm_HandSolder
R7, R34: 12.5k; R_0805_2012Metric_Pad1.20x1.40mm_HandSolder
R8, R9: 5.1k; R_0805_2012Metric_Pad1.20x1.40mm_HandSolder
R12, R15, R16: 28.7; R_2512_6332Metric_Pad1.40x3.35mm_HandSolder
R17, R18, R19: 200; R_0805_2012Metric_Pad1.20x1.40mm_HandSolder
R20, R21, R24: 90k; R_0805_2012Metric_Pad1.20x1.40mm_HandSolder
R22, R26: 180k; R_0805_2012Metric_Pad1.20x1.40mm_HandSolder
R23: 36k; R_0805_2012Metric_Pad1.20x1.40mm_HandSolder
R25: 4.3k; R_0805_2012Metric_Pad1.20x1.40mm_HandSolder
R27: 68k; R_0805_2012Metric_Pad1.20x1.40mm_HandSolder
R28: 510k; R_0805_2012Metric_Pad1.20x1.40mm_HandSolder
R29: 620k; R_0805_2012Metric_Pad1.20x1.40mm_HandSolder
R30: 200k; R_0805_2012Metric_Pad1.20x1.40mm_HandSolder
R31: 51k; R_0805_2012Metric_Pad1.20x1.40mm_HandSolder
R33: 500; R_0805_2012Metric_Pad1.20x1.40mm_HandSolder
R39: 150k; R_0805_2012Metric_Pad1.20x1.40mm_HandSolder
R40: 100k; R_0805_2012Metric_Pad1.20x1.40mm_HandSolder
SW1: Power Switch; PinHeader_1x02_P2.54mm_Vertical
TH1, TH2, TH3: SDNT2012X103F3950FTF; R_0805_2012Metric_Pad1.20x1.40mm_HandSolder
U1: ESP32-D-WD-V3; QFN-48-1EP_5x5mm_P0.35mm_EP3.7x3.7mm
U2, U7, U8: NL17SZ14; SOT-553
U3, U4: DMT3020LSDQ; SO-8_3.9x4.9mm_P1.27mm
U5: LM324; SOIC-14_3.9x8.7mm_P1.27mm
U6, U18: slg55021; TDFN_8_2x2mm_EP_0.9x1.65mm
U9, U10, U11, U20, U21: BSD316; SOT-363_SC-70-6_Handsoldering
U12, U13, U14: PC817; DIP-4_W7.62mm
U15: AS431; SOT-23-5_HandSoldering
U16: AP63203WU; TSOT-23-6
U17: XL6009; TO-263-5_TabPin3
U19: HT75xx-1-SOT89; SOT-89-3
U22: W25Q40CL; SOIC-8W_5.3x5.3mm_P1.27mm
Y1: Crystal_GND24; Crystal_SMD_SeikoEpson_FA238-4Pin_3.2x2.5mm_HandSoldering

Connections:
+3V3: C13.1, C14.1, J6.1, L2.2, R3.1, R20.1, R21.1, R24.1, U16.1 (FB)
+5V: C12.1, J5.1, R2.1, U19.3 (VOUT)
+BATT: BT1.1 (+), C15.1, C21.1, D4.1 (K), R12.1, R22.1, R30.1, SW1.2, U12.4
/MCU/3V3_MCU: C5.1, C8.1, C17.1, J11.1, R3.2, R10.1, U1.1 (VDDA), U1.3 (VDD3P3), U1.4 (VDD3P3), U1.19 (VDD3P3_RTC), U1.43 (VDDA), U1.46 (VDDA), U22.8 (VCC)
/MCU/CELL_DSCHG_1_MCU: R19.2, U1.34 (GPIO5)
/MCU/CELL_DSCHG_2_MCU: R18.2, U1.27 (GPIO17)
/MCU/CELL_DSCHG_3_MCU: R17.2, U1.25 (GPIO16)
/MCU/CELL_MEAS_1_MCU: R28.2, R29.1, U1.22 (GPIO2)
/MCU/CELL_MEAS_2_MCU: R26.2, R27.1, U1.21 (GPIO15/MTDO)
/MCU/CELL_MEAS_3_MCU: R22.2, R23.1, U1.20 (GPIO13/MTCK)
/MCU/DRIVER_DIR_MCU: U1.38 (GPIO19), U2.2 (A), U6.2 (ON), U7.2 (A)
/MCU/DRIVER_EN_MCU: U1.39 (GPIO22), U6.3 (SHDN#), U18.3 (SHDN#)
/MCU/DTR: J10.1, U20.3 (G), U21.4 (S)
/MCU/EN: C16.1, J4.1, R10.2, U1.9 (CHIP_PU), U20.1 (D), U20.2 (D), U20.5 (D), U20.6 (D)
/MCU/IO0: J4.2, U1.23 (GPIO0), U21.1 (D), U21.2 (D), U21.5 (D), U21.6 (D)
/MCU/RTS: J10.2, U20.4 (S), U21.3 (G)
/MCU/RXD_MCU: J9.1, U1.40 (U0RXD)
/MCU/SD_CLK: U1.31 (SD_CLK), U22.6 (CLK)
/MCU/SD_CMD: U1.30 (SD_CMD), U22.1 (~CS)
/MCU/SD_DATA_0: U1.32 (SD_DATA_0), U22.2 (DO)
/MCU/SD_DATA_1: U1.33 (SD_DATA_1), U22.5 (DI)
/MCU/SD_DATA_2: U1.28 (SD_DATA_2), U22.7 (~HOLD)
/MCU/SD_DATA_3: U1.29 (SD_DATA_3), U22.3 (~WP)
/MCU/TEMP_SENSE_1: R20.2, TH1.1, U1.16 (GPIO27)
/MCU/TEMP_SENSE_2: R21.2, TH2.1, U1.15 (GPIO26)
/MCU/TEMP_SENSE_3: R24.2, TH3.1, U1.14 (GPIO25)
/MCU/TXD_MCU: J9.2, U1.41 (U0TXD)
/Peltier Driver/5V_PD: R2.2, U2.5 (VCC), U6.1 (VCC), U7.5 (VCC), U8.5 (VCC), U18.1 (VCC)
GND: C1.2, C2.2, C4.2, C5.2, C6.2, C7.2, C8.2, C9.2, C10.2, C12.2, C13.2, C14.2, C15.2, C16.2, C17.2, C18.2, C21.2, J2.A12 (GND), J2.B12 (GND), J2.S1 (SHIELD), J8.1, J11.2, R4.1, R6.2, R7.2, R8.2, R9.2, R25.2, R27.2, R29.2, R31.2, R39.1, TH1.2, TH2.2, TH3.2, U1.49 (GND_EP), U2.3 (GND), U3.3 (S), U4.3 (S), U5.11 (V-), U6.4 (GND), U7.3 (GND), U8.3 (GND), U12.2, U13.2, U14.2, U15.3, U16.4 (GND), U17.1 (GND), U18.4 (GND), U19.1 (GND), U22.4 (GND), Y1.2, Y1.4
unnamed: AE1.1 (FEED), C1.1, L1.1
unnamed: BT1.2 (-), BT2.1 (+), R15.1, R26.1, U9.4 (S), U13.4
unnamed: BT2.2 (-), BT3.1 (+), R16.1, R28.1, U10.4 (S), U14.4
unnamed: BT3.2 (-), R4.2, R5.2, U11.4 (S)
unnamed: C2.1, L1.2, U1.2 (LNA_IN)
unnamed: C3.1, R1.1, U1.47 (CAP2)
unnamed: C3.2, C4.1, R1.2, U1.48 (CAP1)
unnamed: C6.1, U1.45 (XTAL_P), Y1.1
unnamed: C7.1, U1.44 (XTAL_N), Y1.3
unnamed: C10.1, U1.37 (VDD3P3_CPU)
unnamed: C11.1, L2.1, U16.5 (SW)
unnamed: C11.2, U16.6 (BST)
unnamed: D4.2 (A), L3.2, U17.3 (SW)
unnamed: J1.1, U4.1 (S), U4.5 (D), U4.6 (D), U18.6 (S)
unnamed: J1.2, U3.1 (S), U3.5 (D), U3.6 (D), U6.6 (S)
unnamed: J2.A5 (CC1), R9.1
unnamed: J2.B5 (CC2), R8.1
unnamed: R5.1, R7.1, U5.2 (-)
unnamed: R12.2, U9.1 (D), U9.2 (D), U9.5 (D), U9.6 (D)
unnamed: R15.2, U10.1 (D), U10.2 (D), U10.5 (D), U10.6 (D)
unnamed: R16.2, U11.1 (D), U11.2 (D), U11.5 (D), U11.6 (D)
unnamed: R17.1, U12.1
unnamed: R18.1, U13.1
unnamed: R19.1, U14.1
unnamed: R23.2, R25.1
unnamed: R30.2, R31.1, U5.6 (-)
unnamed: R33.2, U5.5 (+), U15.1, U15.2
unnamed: R6.1, R34.1, U5.3 (+)
unnamed: R34.2, U5.1, U17.5 (FB)
unnamed: R39.2, R40.1, U1.11 (GPIO35/VDET_2)
unnamed: C18.1, U1.26 (VDD_SDIO)
unnamed: U2.4 (Y), U3.4 (G)
unnamed: U3.2 (G), U6.7 (G)
unnamed: U4.4 (G), U8.4 (Y)
unnamed: U10.3 (G), U13.3
unnamed: U11.3 (G), U14.3
unnamed: U9.3 (G), U12.3
unnamed: U5.7, U17.2 (EN)
unnamed: U7.4 (Y), U8.2 (A), U18.2 (ON)
unnamed: U4.2 (G), U18.7 (G)
PWR_UNREG: C9.1, J3.1, SW1.1, U3.7 (D), U3.8 (D), U4.7 (D), U4.8 (D), U6.5 (D), U16.2 (EN), U16.3 (IN), U18.5 (D), U19.2 (VIN)
VBUS: J2.A9 (VBUS), J2.B9 (VBUS), J7.1, L3.1, R33.1, R40.2, U5.4 (V+), U17.4 (VIN)

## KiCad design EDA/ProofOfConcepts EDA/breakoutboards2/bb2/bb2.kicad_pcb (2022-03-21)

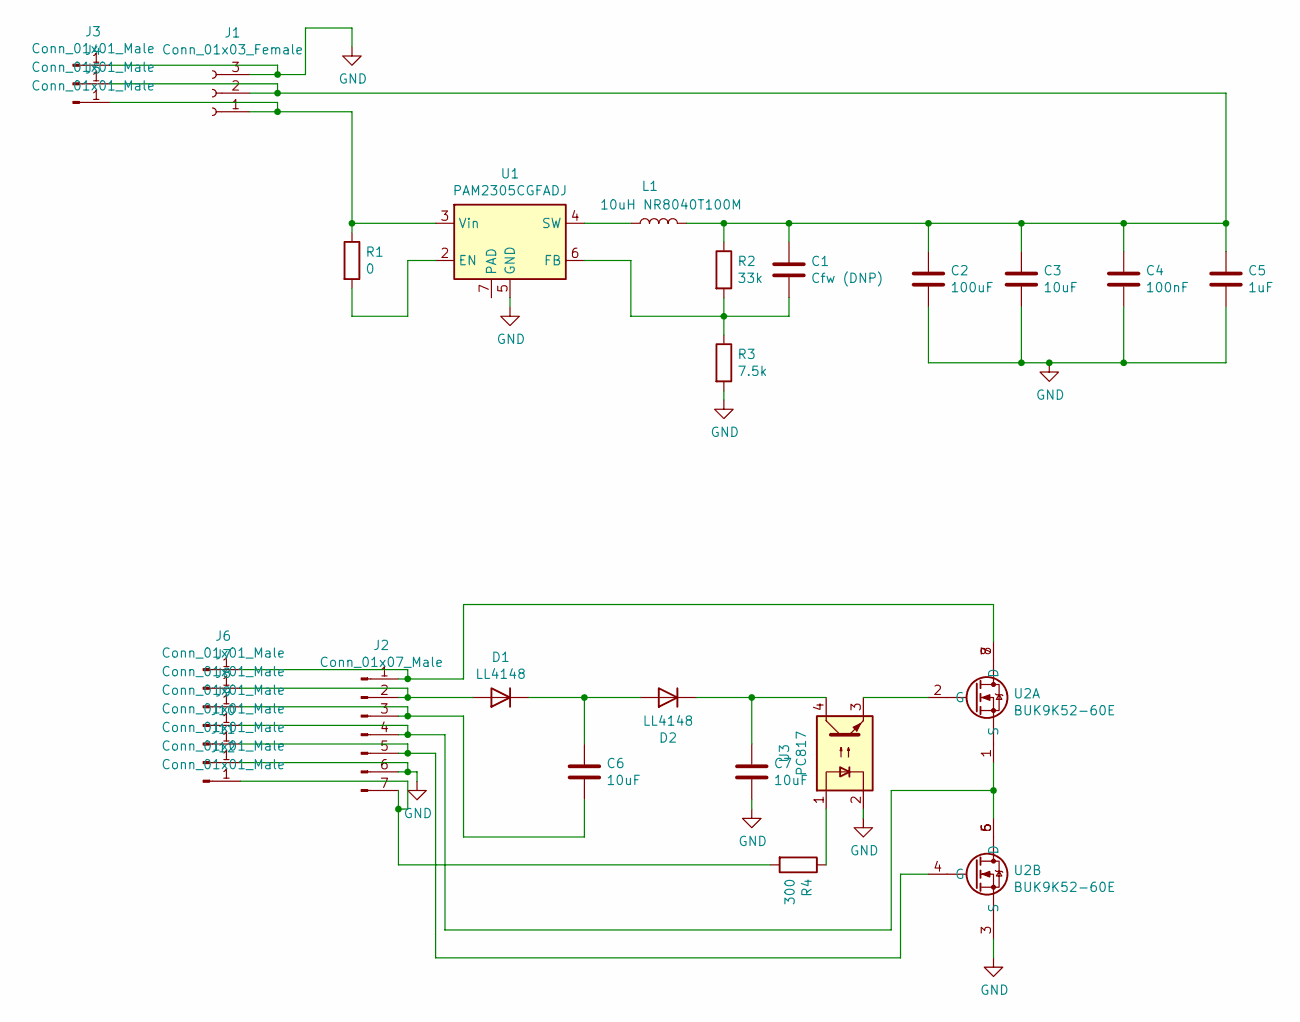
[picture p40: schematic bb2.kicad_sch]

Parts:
C1: Cfw (DNP); C_0805_2012Metric_Pad1.18x1.45mm_HandSolder
C2: 100uF; C_1210_3225Metric_Pad1.33x2.70mm_HandSolder
C3, C6, C7: 10uF; C_0805_2012Metric_Pad1.18x1.45mm_HandSolder
C4: 100nF; C_0805_2012Metric_Pad1.18x1.45mm_HandSolder
C5: 1uF; C_0805_2012Metric_Pad1.18x1.45mm_HandSolder
D1, D2: LL4148; D_MiniMELF
J1: Conn_01x03_Female; PinHeader_1x03_P2.54mm_Vertical
J2: Conn_01x07_Male; PinHeader_1x07_P2.54mm_Vertical
J3, J4, J5, J6, J7, J8, J9, J10, J11, J12: Conn_01x01_Male; GatorTestpoint
L1: 10uH NR8040T100M; L_Taiyo-Yuden_NR-80xx_HandSoldering
R1: 0; R_0805_2012Metric_Pad1.20x1.40mm_HandSolder
R2: 33k; R_0805_2012Metric_Pad1.20x1.40mm_HandSolder
R3: 7.5k; R_0805_2012Metric_Pad1.20x1.40mm_HandSolder
R4: 300; R_0805_2012Metric_Pad1.20x1.40mm_HandSolder
U1: PAM2305CGFADJ; DFN-6-1EP_2x2mm_P0.65mm_EP1x1.6mm
U2: BUK9K52-60E; LFPAK56D
U3: PC817; SOP-4_3.8x4.1mm_P2.54mm

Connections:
GND: C2.2, C3.2, C4.2, C5.2, C7.2, J1.3, J2.6, J3.1, J11.1, R3.2, U1.5 (GND), U2.3 (S), U3.2
unnamed: C1.1, C2.1, C3.1, C4.1, C5.1, J1.2, J4.1, L1.2, R2.1
unnamed: C1.2, R2.2, R3.1, U1.6 (FB)
unnamed: C6.1, D1.1 (K), D2.2 (A)
unnamed: C6.2, J2.3, J8.1
unnamed: C7.1, D2.1 (K), U3.4
unnamed: D1.2 (A), J2.2, J7.1
unnamed: J1.1, J5.1, R1.1, U1.3 (Vin)
unnamed: J2.1, J6.1, U2.7 (D), U2.8 (D)
unnamed: J2.4, J9.1, U2.1 (S), U2.5 (D), U2.6 (D)
unnamed: J2.5, J10.1, U2.4 (G)
unnamed: J2.7, J12.1, R4.2
unnamed: L1.1, U1.4 (SW)
unnamed: R1.2, U1.2 (EN)
unnamed: R4.1, U3.1
unnamed: U2.2 (G), U3.3

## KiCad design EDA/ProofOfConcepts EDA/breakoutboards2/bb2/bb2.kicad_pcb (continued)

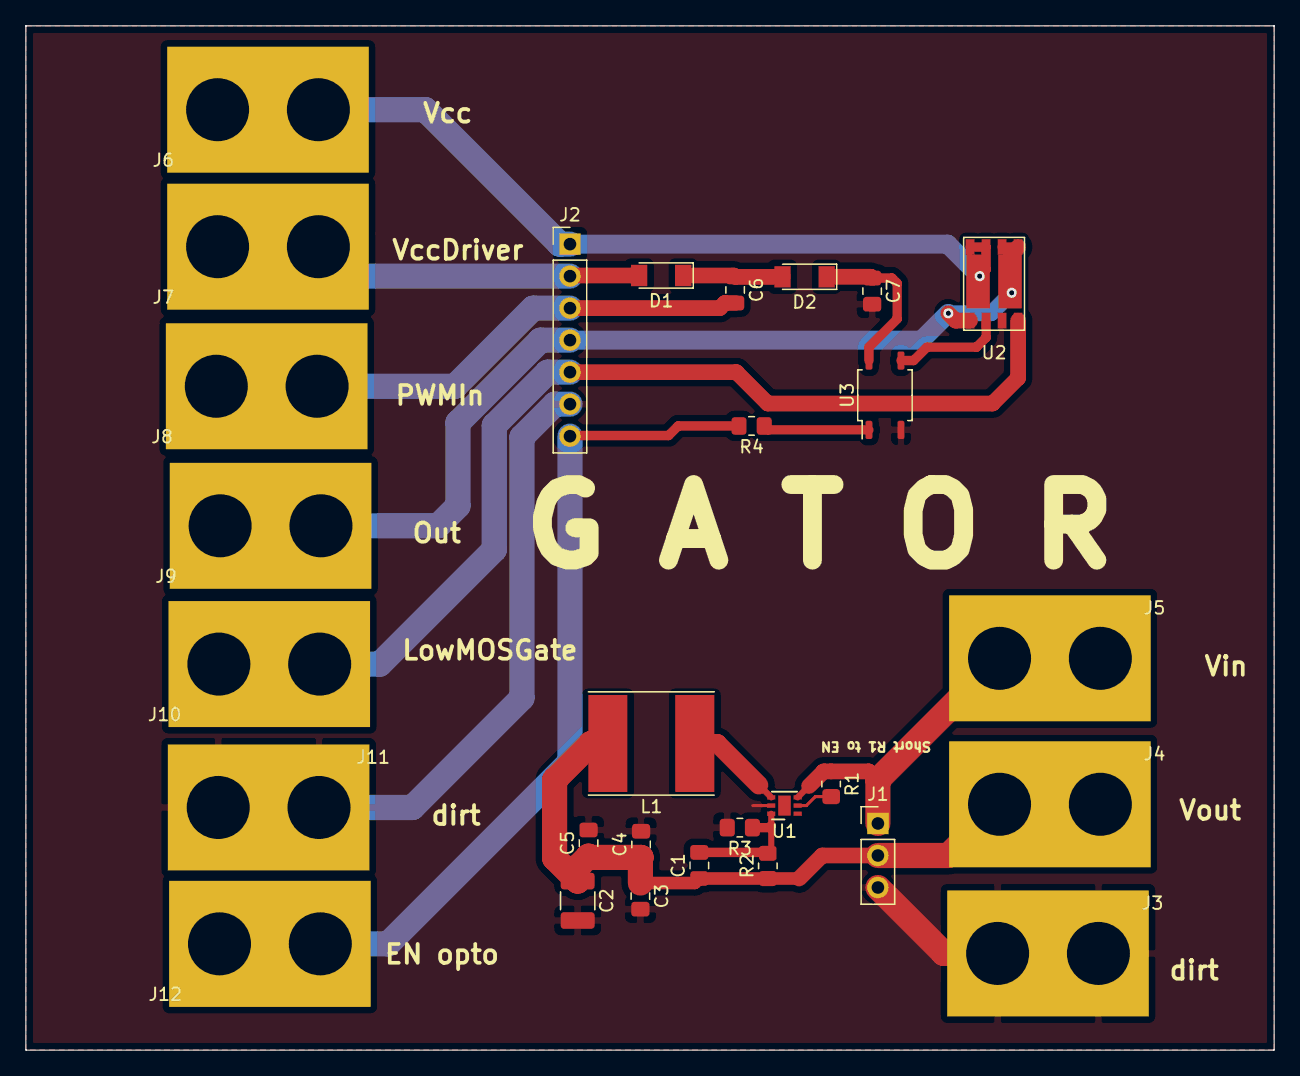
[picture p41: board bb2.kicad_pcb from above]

Board: 2 copper layers, 99.1 x 81.3 mm, 29 parts (0 on the bottom side), 16 nets.

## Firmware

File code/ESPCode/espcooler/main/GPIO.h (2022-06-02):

#ifndef GPIO_H_
#define GPIO_H_

#define HIGH 1
#define LOW 0
#define INPUT 1
#define OUTPUT 0



#define PWR_SW_PIN 14
#define USB_PWR_DETECT_PIN 35


#define CELL_1_DISCHG_PIN 5
#define CELL_2_DISCHG_PIN 17
#define CELL_3_DISCHG_PIN 16
#define DRIVER_EN_PIN 22
#define DRIVER_DIR_PIN 19


/**********************************************
 * write_pin
 * writes to the specified digital pin
 * 
 *********************************************/
void write_pin(uint8_t digital_pin, uint8_t lvl);


/**********************************************
 * read_pin
 * reads from the specified digital pin
 * 
 *********************************************/
uint8_t read_pin(uint8_t digital_pin);

/**********************************************
 * init_pin
 * reads from the specified digital pin
 * 
 *********************************************/
void init_pin(uint8_t digital_pin, uint8_t pinMode);
#endif

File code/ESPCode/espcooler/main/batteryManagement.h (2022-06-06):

#ifndef BATTERYMANAGEMENT_H_
#define BATTERYMANAGEMENT_H_

#define MAX_CELL_VOLTAGE_DIFF .02


//#define TWO_CELL      //uncomment for only 2 cells

//cell voltage measurement 1/divider ratios
#define CELL_1_VOLTIGE_DIV_RATIO ((510.0 + 620.0) / 620.0)
#define CELL_2_VOLTIGE_DIV_RATIO ((180.0 + 68.0) / 68.0)
#define CELL_3_VOLTIGE_DIV_RATIO ((180.0 + 40.3) / 40.3)

//li-ion capabilities
#define MIN_CELL_VOLTAGE 3.7
#define MAX_CELL_VOLTAGE 4.1

/*******************************
 * batteryManagementInit
 * call at startup to start detect charger and perform cell balancing
 ******************************/
void batteryManagementInit(uint8_t PRIORITY);


/*******************************
 * get_battery_level
 * returns battery level in single percents
 ******************************/
uint8_t get_battery_level();

#endif

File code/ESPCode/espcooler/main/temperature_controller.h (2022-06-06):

#ifndef TEMPERATURE_CONTROLLER_H_
#define TEMPERATURE_CONTROLLER_H_


//#define PELTIER_INVERT //uncomment to invert peltier pins (hot/cold)

//temperature params

//temperature limits, degrees C
//limits of insulin are 2.22 to 7.778 degrees C
#define MAX_TEMPERATURE (273.15 + 7)
#define MIN_TEMPERATURE (273.15 + 3)
#define MID_TEMPERATURE ((((float)MAX_TEMPERATURE - (float)MIN_TEMPERATURE) / 2.00) + (float)MIN_TEMPERATURE)


//pwm cycles. duty cycle = 1/PELTIER_PWM * 100 %
#define PELTIER_PWM 3
//calcs
#define PELTIER_PWM_COUNT (uint8_t)PELTIER_PWM

#define KELVIN 273.15
//beta value for ntc resistor
#define NTC_B 3950
//R value at T0
#define NTC_R 10000
//T0 temperature celcius
#define NTC_T0 (KELVIN + 25)
//R1 value, the other resistor in the divider
#define R1 10000
//voltage of the north of voltage divider
#define VCC 3.3

#define C1 (NTC_R * exp(-(NTC_B/NTC_T0)))




/***************************************************************
 * temperate controller intialization
 * initializes the ADC, GPIO/PWM
 **************************************************************/
void temp_control_init(int8_t PRIORITY);


/***************************************************************
 * get_peltier_temperature
 * returns the temperature in kelvins
 **************************************************************/
float get_peltier_temperature();
/***************************************************************
 * peltier_temperature_ready
 * returns the state of the mutex of the temperature
 **************************************************************/
uint8_t peltier_temperature_ready();

#endif

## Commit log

2022-01-26 e
    e
    [Part1.ipt, schematic.kicad_pcb, schematic.sch]
2022-01-31 schematic done
    [MCU.sch, driver.sch, main.0001.ipt, main.ipt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]
2022-02-15 fixed vias
    [schematic.kicad_pcb]
2022-02-19 gerber push
    [schematic-B_Cu.gbr, schematic-B_Mask.gbr, schematic-B_Paste.gbr, schematic-B_SilkS.gbr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]
2022-03-04 updated resistor dividers for more friendly values
    [pwrmngmt.sch, schematic.sch]
2022-03-05 Create charge pump simulation.cmf
2022-03-06 replacing buck converter with higher efficiency one
    [bb2.kicad_pcb, bb2.sch, pwrmngmt.sch]
2022-03-08 breakout board for v2 buck and nmos driver
    [bb2-B_Cu.gbr, bb2-B_Mask.gbr, bb2-B_Paste.gbr, bb2-B_SilkS.gbr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]
2022-03-19 final winter qtr push
    [ChargerPOC.kicad_pcb, ChargerPOC.kicad_sch, MCU.kicad_sch, bb2.kicad_pcb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]
2022-03-31 reorg + course docs
    [ReqExcelVersionTemplate.xlsx, schematic-B_Cu.gbr, schematic-B_Mask.gbr, schematic-B_Paste.gbr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]
2022-04-11 beta boards routed
    [HI.kicad_sch, driver.kicad_sch, gatorports.kicad_sch, pwrmngmt.kicad_sch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]
2022-04-22 prelim ble working
    [MCU.kicad_sch, pwrmngmt.kicad_sch, schematic-B_Cu.gbr, schematic-B_Mask.gbr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]
2022-06-02 code done ish
    [InsulinCoolerBoard.kicad_sch, pwrmngmt.kicad_sch, tempsensor.kicad_sch]
